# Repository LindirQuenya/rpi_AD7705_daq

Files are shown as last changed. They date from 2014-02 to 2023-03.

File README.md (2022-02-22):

# Data acquisition with the AD7705 on the raspberry PI!

The AD7705 is a two channel sigma delta converter which has
differential inputs, a PGA and programmable data rates. It's
perfect for slowly changing inputs such as pressure, temperature,
heart rate etc.

This repo offers the class `AD7705Comm` which does all the low level
communications with the AD7705. The user just need to register a
callback handler which then returns the samples in realtime.

The class uses the DRDY of the AD7705 connected to Port 22 and
waits for a falling edge on this port to read
the data. This is done via interrupts / poll
so that the ADC process sleeps until new data becomes
available.

## Hardware design

The design files (for EAGLE) are in the subdirectory "pcb".

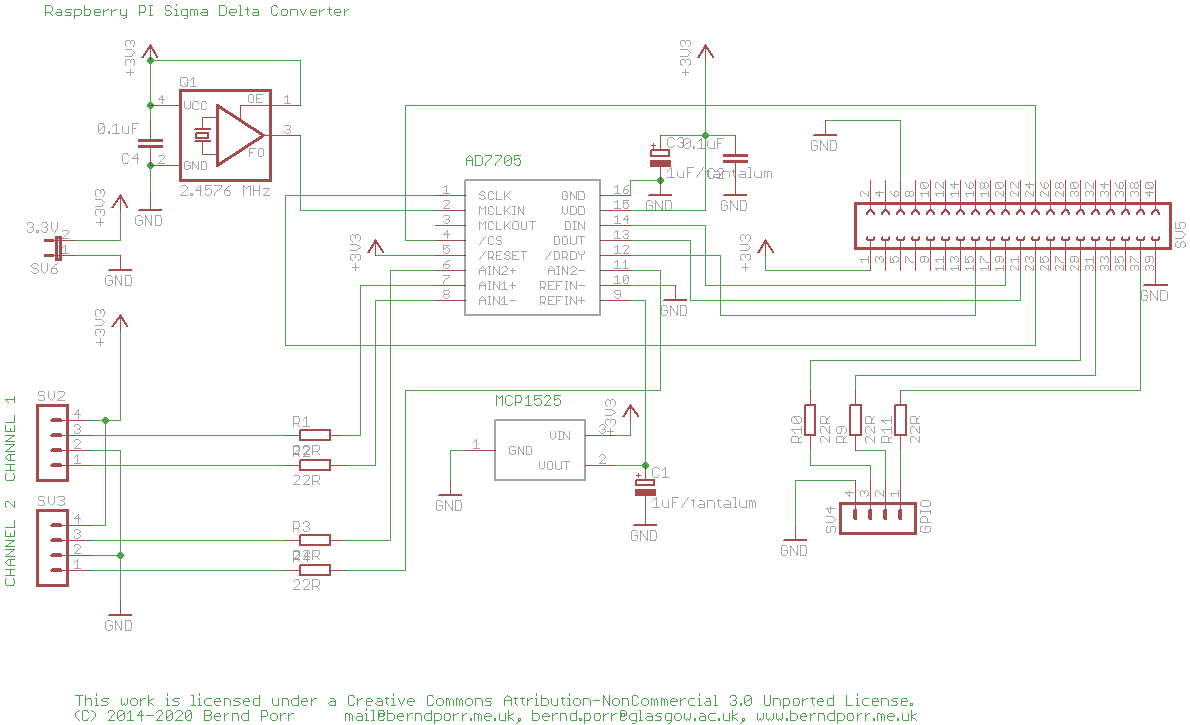
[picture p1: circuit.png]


## Building:

To build:

    cmake .

    make

## Install

    sudo make install

## Usage example

In the subdir example is a simple application which prints the ADC data to the screen.

    cd example
    sudo ./ad7705_printer

## General usage

The online doc is here: http://berndporr.github.io/rpi_AD7705_daq/

### Callback handler

```
class AD7705printSampleCallback : public AD7705callback {
	virtual void hasSample(float v) {
		// process your sample here
	}
};
```

### Main program

Instantiate the AD7705 class and the callback handler:
```
	AD7705Comm ad7705comm;
	AD7705printSampleCallback ad7705printSampleCallback;
	ad7705comm.setCallback(&ad7705printSampleCallback);
```

Start the data acquisition:
```
	ad7705comm.start();
```
once `start` has been called the data will be arriving.

Stop the data acquisition:
```
	ad7705comm.stop();
```

## Author: Bernd Porr

   - bernd.porr@glasgow.ac.uk
   - mail@berndporr.me.uk
   - www.berndporr.me.uk

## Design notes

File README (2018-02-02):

Test / demo program for the AD7705 connected to the raspberry PI!
=================================================================

The AD7705 is a two channel sigma delta converter which has
differential inputs, a PGA and programmable data rates. It's
perfect for slowly changing inputs such as pressure, temperature,
heart rate etc.

The program is interrupt driven and can thus run in a thread
which is woken up by the interrupt. The clock for the ADC is
generated by directly manipulating the registers of the BCM
chip.

This program switches on the clock from the RPI, 
triggers a calibration of the AD, 
reads data from channel 1 and 
prints it on the screen.

This program uses DRDY connected to Port 22 and
waits for a falling edge on this port to read
the data. This is done via interrupts / poll
so that this process sleeps until new data becomes
available.

The design files are in the subdirectory "pcb".



To build:

    make

Run it with the command:

    sudo ./ad7705_test

Associated website:
http://web.eng.gla.ac.uk/rpi/

Bernd Porr
mail@berndporr.me.uk
www.berndporr.me.uk

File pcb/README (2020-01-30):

This work is licensed under a Creative Commons Attribution-NonCommercial 3.0 Unported License.
(C) 2013-2020 BERND PORR, www.berndporr.me.uk

This is an extension board which adds two analogue inputs to the Raspberry PI.
Three GPIO pins are also forwarded to another pin header with additional
input protection.

The AD7705 is a high preceision sigma delta converter with differential
inputs, buffers and a PGA. It's especially designed to measure small voltages,
for example from a pressure gauge or a thermocpuple.

The maximum sampling rate is 500Hz.

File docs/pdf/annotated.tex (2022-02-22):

\doxysection{Class List}
Here are the classes, structs, unions and interfaces with brief descriptions\+:\begin{DoxyCompactList}
\item\contentsline{section}{\mbox{\hyperlink{classAD7705callback}{A\+D7705callback}} \\*Callback for new samples which needs to be implemented by the main program }{\pageref{classAD7705callback}}{}
\item\contentsline{section}{\mbox{\hyperlink{classAD7705Comm}{A\+D7705\+Comm}} \\*This class reads data from the A\+D7705 in the background (separate thread) and calls a callback function whenever data is available }{\pageref{classAD7705Comm}}{}
\item\contentsline{section}{\mbox{\hyperlink{structAD7705settings}{A\+D7705settings}} \\*Contains all settings for the data acquisition }{\pageref{structAD7705settings}}{}
\end{DoxyCompactList}

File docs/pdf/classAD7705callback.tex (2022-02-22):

\hypertarget{classAD7705callback}{}\doxysection{A\+D7705callback Class Reference}
\label{classAD7705callback}\index{AD7705callback@{AD7705callback}}

Callback for new samples which needs to be implemented by the main program.  

{\ttfamily \#include $<$A\+D7705\+Comm.\+h$>$}

\doxysubsection*{Public Member Functions}
\begin{DoxyCompactItemize}
\item 
virtual void \mbox{\hyperlink{classAD7705callback_a0af40415519aef054c0934f6548bab33}{has\+Sample}} (float sample)=0
\begin{DoxyCompactList}\small\item\em Called after a sample has arrived. \end{DoxyCompactList}\end{DoxyCompactItemize}

\doxysubsection{Detailed Description}
Callback for new samples which needs to be implemented by the main program. 

The function has\+Sample needs to be overloaded in the main program. 

\doxysubsection{Member Function Documentation}
\mbox{\Hypertarget{classAD7705callback_a0af40415519aef054c0934f6548bab33}\label{classAD7705callback_a0af40415519aef054c0934f6548bab33}} 
\index{AD7705callback@{AD7705callback}!hasSample@{hasSample}}
\index{hasSample@{hasSample}!AD7705callback@{AD7705callback}}
\doxysubsubsection{\texorpdfstring{hasSample()}{hasSample()}}
{\footnotesize\ttfamily virtual void A\+D7705callback\+::has\+Sample (\begin{DoxyParamCaption}\item[{float}]{sample }\end{DoxyParamCaption})\hspace{0.3cm}{\ttfamily [pure virtual]}}

Called after a sample has arrived. 

\begin{DoxyParams}{Parameters}
{\em sample} & Contains the A\+DC reading in Volt. \\
\hline
\end{DoxyParams}

The documentation for this class was generated from the following file\+:\begin{DoxyCompactItemize}
\item 
A\+D7705\+Comm.\+h\end{DoxyCompactItemize}

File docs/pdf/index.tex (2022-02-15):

The A\+D7705 is a two channel sigma delta converter which has differential inputs, a P\+GA and programmable data rates. It\textquotesingle{}s perfect for slowly changing inputs such as pressure, temperature, heart rate etc.

This repo offers the class {\ttfamily \mbox{\hyperlink{classAD7705Comm}{A\+D7705\+Comm}}} which does all the low level communications with the A\+D7705. The user just need to register a callback handler which then returns the samples in realtime.

The class uses the D\+R\+DY of the A\+D7705 connected to Port 22 and waits for a falling edge on this port to read the data. This is done via interrupts / poll so that the A\+DC process sleeps until new data becomes available.

Github\+: \href{https://github.com/berndporr/rpi_AD7705_daq}{\texttt{ https\+://github.\+com/berndporr/rpi\+\_\+\+A\+D7705\+\_\+daq}}

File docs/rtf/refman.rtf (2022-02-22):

Data acquisition with the AD7705 on the raspberry PI

AUTHOR
Version
Tue Feb 22 2022

Table of Contents

Table of contents

Data acquisition with the AD7705 on the raspberry PI!
The AD7705 is a two channel sigma delta converter which has differential inputs, a PGA and programmable data rates. It's perfect for slowly changing inputs such as pressure, temperature, heart rate etc.
This repo offers the class AD7705Comm which does all the low level communications with the AD7705. The user just need to register a callback handler which then returns the samples in realtime.
The class uses the DRDY of the AD7705 connected to Port 22 and waits for a falling edge on this port to read the data. This is done via interrupts / poll so that the ADC process sleeps until new data becomes available.
Github: https://github.com/berndporr/rpi_AD7705_daq

Class Index
Class List
Here are the classes, structs, unions and interfaces with brief descriptions:
AD7705callback (Callback for new samples which needs to be implemented by the main program ) pagenum
AD7705Comm (This class reads data from the AD7705 in the background (separate thread) and calls a callback function whenever data is available ) pagenum
AD7705settings (Contains all settings for the data acquisition ) pagenum

Class Documentation
AD7705callback Class Reference
AAAAAAAAAAAAAAAAAAAA
Callback for new samples which needs to be implemented by the main program.
#include <AD7705Comm.h>

Public Member Functions
virtual void hasSample (float sample)=0
Called after a sample has arrived.

Detailed Description
Callback for new samples which needs to be implemented by the main program.
The function hasSample needs to be overloaded in the main program.

Member Function Documentation
virtual void AD7705callback::hasSample (float sample)[pure virtual]
AAAAAAAAABAAAAAAAAAB
Called after a sample has arrived.

Parameters
sample | Contains the ADC reading in Volt.

The documentation for this class was generated from the following file:
AD7705Comm.h

AD7705Comm Class Reference
AAAAAAAAACAAAAAAAAAC
This class reads data from the AD7705 in the background (separate thread) and calls a callback function whenever data is available.
#include <AD7705Comm.h>

Public Member Functions
AD7705Comm (AD7705settings settings)
Constructor.

~AD7705Comm ()AAAAAAAAADAAAAAAAAAD
Destructor which makes sure the data acquisition has stopped.

void registerCallback (AD7705callback *cb)
Registers the callback which is called whenever there is a sample.

void unRegisterCallback ()AAAAAAAAAEAAAAAAAAAE
Unregisters the callback to the callback interface.

void start ()AAAAAAAAAFAAAAAAAAAF
Starts the data acquisition.

void stop ()AAAAAAAAAGAAAAAAAAAG
Stops the data acquistion.

Detailed Description
This class reads data from the AD7705 in the background (separate thread) and calls a callback function whenever data is available.

Constructor & Destructor Documentation
AD7705Comm::AD7705Comm (AD7705settings settings)
AAAAAAAAAHAAAAAAAAAH
Constructor.
Opens the SPI device and waits for to start the acquisition.
Parameters
settings | All AD7705 settings.

Member Function Documentation
void AD7705Comm::registerCallback (AD7705callback * cb)
AAAAAAAAAIAAAAAAAAAI
Registers the callback which is called whenever there is a sample.

Parameters
cb | Pointer to the callback interface.

The documentation for this class was generated from the following file:
AD7705Comm.h

AD7705settings Struct Reference
AAAAAAAAAJAAAAAAAAAJ
Contains all settings for the data acquisition.
#include <AD7705Comm.h>

Public Types
enum SamplingRates { FS50HZ = 0, FS60HZ = 1, FS250HZ = 2, FS500HZ = 3 }AAAAAAAAAKAAAAAAAAAK
Sampling rates.
enum PGAGains { G1 = 0, G2 = 1, G4 = 2, G8 = 3, G16 = 4, G32 = 5, G64 = 6, G128 = 7 }AAAAAAAAALAAAAAAAAAL
Gains of the PGA.
enum AIN { AIN1 = 0, AIN2 = 1 }AAAAAAAAAMAAAAAAAAAM
Channel indices.
enum Modes { Bipolar = 0, Unipolar = 1 }AAAAAAAAANAAAAAAAAAN
Unipolar or bipolar mode.
Public Attributes
std::string spiDevice = "/dev/spidev0.0"AAAAAAAAAOAAAAAAAAAO
The SPI device in /dev used.

SamplingRates samplingRate = FS50HZAAAAAAAAAPAAAAAAAAAP
Sampling rate requested.

PGAGains pgaGain = G1AAAAAAAAAQAAAAAAAAAQ
Requested gain.

AIN channel = AIN1AAAAAAAAARAAAAAAAAAR
Requested input channel (0 or 1)

Modes mode = UnipolarAAAAAAAAASAAAAAAAAAS
Unipolar or biploar.

Detailed Description
Contains all settings for the data acquisition.

The documentation for this struct was generated from the following file:
AD7705Comm.h

Index
INDEX

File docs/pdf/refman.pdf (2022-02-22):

## Data acquisition with the AD7705 on the raspberry PI

Generated by Doxygen 1.8.17

i

1 Data acquisition with the AD7705 on the raspberry PI! | 1
2 Class Index | 3
3 Class Documentation | 5
Index | 9

Generated by Doxygen

# Chapter 1

# Data acquisition with the AD7705 on the raspberry

PI!

The AD7705 is a two channel sigma delta converter which has differential inputs, a PGA and programmable data rates. It's perfect for slowly changing inputs such as pressure, temperature, heart rate etc.

This repo offers the class AD7705Comm which does all the low level communications with the AD7705. The user just need to register a callback handler which then returns the samples in realtime.

The class uses the DRDY of the AD7705 connected to Port 22 and waits for a falling edge on this port to read the data. This is done via interrupts / poll so that the ADC process sleeps until new data becomes available.

Github: https://github.com/berndporr/rpi_AD7705_daq

### 2 Data acquisition with the AD7705 on the raspberry PI!

# Chapter 2

# Class Index

## 2.1 Class List

Here are the classes, structs, unions and interfaces with brief descriptions:

AD7705callback

AD7705Comm
This class reads data from the AD7705 in the background (separate thread) and calls a callback

AD7705settings

### 4 Class Index

# Chapter 3

# Class Documentation

## 3.1 AD7705callback Class Reference

Callback for new samples which needs to be implemented by the main program.

#include <AD7705Comm.h>

Public Member Functions

- virtual void hasSample (float sample)=0

Called after a sample has arrived.

### 3.1.1 Detailed Description

Callback for new samples which needs to be implemented by the main program.

The function hasSample needs to be overloaded in the main program.

### 3.1.2 Member Function Documentation

### 3.1.2.1 hasSample()

virtual void AD7705callback::hasSample (

float sample ) [pure virtual]

Called after a sample has arrived.

Parameters

sample Contains the ADC reading in Volt.

### 6 Class Documentation

The documentation for this class was generated from the following file:

- AD7705Comm.h

## 3.2 AD7705Comm Class Reference

This class reads data from the AD7705 in the background (separate thread) and calls a callback function whenever data is available.

#include <AD7705Comm.h>

Public Member Functions

- AD7705Comm (AD7705settings settings)

Constructor.
- ∼AD7705Comm ()

Destructor which makes sure the data acquisition has stopped.
- void registerCallback (AD7705callback ∗cb)

Registers the callback which is called whenever there is a sample.
- void unRegisterCallback ()

Unregisters the callback to the callback interface.
- void start ()

Starts the data acquisition.
- void stop ()

Stops the data acquistion.

### 3.2.1 Detailed Description

This class reads data from the AD7705 in the background (separate thread) and calls a callback function whenever data is available.

### 3.2.2 Constructor & Destructor Documentation

### 3.2.2.1 AD7705Comm()

AD7705Comm::AD7705Comm (

AD7705settings settings )

Constructor.

Opens the SPI device and waits for to start the acquisition.

3.3 AD7705settings Struct Reference | 7

Parameters

settings All AD7705 settings.

### 3.2.3 Member Function Documentation

### 3.2.3.1 registerCallback()

void AD7705Comm::registerCallback (

AD7705callback ∗ cb )

Registers the callback which is called whenever there is a sample.

Parameters

cb Pointer to the callback interface.

The documentation for this class was generated from the following file:

- AD7705Comm.h

## 3.3 AD7705settings Struct Reference

Contains all settings for the data acquisition.

#include <AD7705Comm.h>

Public Types

- enum SamplingRates { FS50HZ = 0, FS60HZ = 1, FS250HZ = 2, FS500HZ = 3 }

Sampling rates.
- enum PGAGains {
G1 = 0, G2 = 1, G4 = 2, G8 = 3,
G16 = 4, G32 = 5, G64 = 6, G128 = 7 }

Gains of the PGA.
- enum AIN { AIN1 = 0, AIN2 = 1 }

Channel indices.
- enum Modes { Bipolar = 0, Unipolar = 1 }

Unipolar or bipolar mode.

### 8 Class Documentation

Public Attributes

- std::string spiDevice = "/dev/spidev0.0"

The SPI device in /dev used.
- SamplingRates samplingRate = FS50HZ

Sampling rate requested.
- PGAGains pgaGain = G1

Requested gain.
- AIN channel = AIN1

Requested input channel (0 or 1)
- Modes mode = Unipolar

Unipolar or biploar.

### 3.3.1 Detailed Description

Contains all settings for the data acquisition.

The documentation for this struct was generated from the following file:

- AD7705Comm.h

# Index

AD7705callback, 5
hasSample, 5
AD7705Comm, 6
AD7705Comm, 6
registerCallback, 7
AD7705settings, 7

hasSample
AD7705callback, 5

registerCallback
AD7705Comm, 7

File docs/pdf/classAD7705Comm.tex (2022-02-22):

\hypertarget{classAD7705Comm}{}\doxysection{A\+D7705\+Comm Class Reference}
\label{classAD7705Comm}\index{AD7705Comm@{AD7705Comm}}

This class reads data from the A\+D7705 in the background (separate thread) and calls a callback function whenever data is available.  

{\ttfamily \#include $<$A\+D7705\+Comm.\+h$>$}

\doxysubsection*{Public Member Functions}
\begin{DoxyCompactItemize}
\item 
\mbox{\hyperlink{classAD7705Comm_a1d06fa3bdea3ee1616dcab0f406aca8a}{A\+D7705\+Comm}} (\mbox{\hyperlink{structAD7705settings}{A\+D7705settings}} settings)
\begin{DoxyCompactList}\small\item\em Constructor. \end{DoxyCompactList}\item 
\mbox{\Hypertarget{classAD7705Comm_a6f101db8298da94c1bb82c2735015eb1}\label{classAD7705Comm_a6f101db8298da94c1bb82c2735015eb1}} 
\mbox{\hyperlink{classAD7705Comm_a6f101db8298da94c1bb82c2735015eb1}{$\sim$\+A\+D7705\+Comm}} ()
\begin{DoxyCompactList}\small\item\em Destructor which makes sure the data acquisition has stopped. \end{DoxyCompactList}\item 
void \mbox{\hyperlink{classAD7705Comm_a3bf730b355147bde014465c37b17623a}{register\+Callback}} (\mbox{\hyperlink{classAD7705callback}{A\+D7705callback}} $\ast$cb)
\begin{DoxyCompactList}\small\item\em Registers the callback which is called whenever there is a sample. \end{DoxyCompactList}\item 
\mbox{\Hypertarget{classAD7705Comm_a302b3a43102d7675a4f27382f388d1b4}\label{classAD7705Comm_a302b3a43102d7675a4f27382f388d1b4}} 
void \mbox{\hyperlink{classAD7705Comm_a302b3a43102d7675a4f27382f388d1b4}{un\+Register\+Callback}} ()
\begin{DoxyCompactList}\small\item\em Unregisters the callback to the callback interface. \end{DoxyCompactList}\item 
\mbox{\Hypertarget{classAD7705Comm_affc6ded162b91b5e55ed791451ef2373}\label{classAD7705Comm_affc6ded162b91b5e55ed791451ef2373}} 
void \mbox{\hyperlink{classAD7705Comm_affc6ded162b91b5e55ed791451ef2373}{start}} ()
\begin{DoxyCompactList}\small\item\em Starts the data acquisition. \end{DoxyCompactList}\item 
\mbox{\Hypertarget{classAD7705Comm_a6817c77451e4a0f7a85a79c1c39d158e}\label{classAD7705Comm_a6817c77451e4a0f7a85a79c1c39d158e}} 
void \mbox{\hyperlink{classAD7705Comm_a6817c77451e4a0f7a85a79c1c39d158e}{stop}} ()
\begin{DoxyCompactList}\small\item\em Stops the data acquistion. \end{DoxyCompactList}\end{DoxyCompactItemize}

\doxysubsection{Detailed Description}
This class reads data from the A\+D7705 in the background (separate thread) and calls a callback function whenever data is available. 

\doxysubsection{Constructor \& Destructor Documentation}
\mbox{\Hypertarget{classAD7705Comm_a1d06fa3bdea3ee1616dcab0f406aca8a}\label{classAD7705Comm_a1d06fa3bdea3ee1616dcab0f406aca8a}} 
\index{AD7705Comm@{AD7705Comm}!AD7705Comm@{AD7705Comm}}
\index{AD7705Comm@{AD7705Comm}!AD7705Comm@{AD7705Comm}}
\doxysubsubsection{\texorpdfstring{AD7705Comm()}{AD7705Comm()}}
{\footnotesize\ttfamily A\+D7705\+Comm\+::\+A\+D7705\+Comm (\begin{DoxyParamCaption}\item[{\mbox{\hyperlink{structAD7705settings}{A\+D7705settings}}}]{settings }\end{DoxyParamCaption})}

Constructor. 

Opens the S\+PI device and waits for to start the acquisition. 
\begin{DoxyParams}{Parameters}
{\em settings} & All A\+D7705 settings. \\
\hline
\end{DoxyParams}

\doxysubsection{Member Function Documentation}
\mbox{\Hypertarget{classAD7705Comm_a3bf730b355147bde014465c37b17623a}\label{classAD7705Comm_a3bf730b355147bde014465c37b17623a}} 
\index{AD7705Comm@{AD7705Comm}!registerCallback@{registerCallback}}
\index{registerCallback@{registerCallback}!AD7705Comm@{AD7705Comm}}
\doxysubsubsection{\texorpdfstring{registerCallback()}{registerCallback()}}
{\footnotesize\ttfamily void A\+D7705\+Comm\+::register\+Callback (\begin{DoxyParamCaption}\item[{\mbox{\hyperlink{classAD7705callback}{A\+D7705callback}} $\ast$}]{cb }\end{DoxyParamCaption})}

Registers the callback which is called whenever there is a sample. 

\begin{DoxyParams}{Parameters}
{\em cb} & Pointer to the callback interface. \\
\hline
\end{DoxyParams}

The documentation for this class was generated from the following file\+:\begin{DoxyCompactItemize}
\item 
A\+D7705\+Comm.\+h\end{DoxyCompactItemize}

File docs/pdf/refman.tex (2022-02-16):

\let\mypdfximage\pdfximage\def\pdfximage{\immediate\mypdfximage}\documentclass[twoside]{book}

%% moved from doxygen.sty due to workaround for LaTex 2019 version and unmaintained tabu package
\usepackage{ifthen}
\ifx\requestedLaTeXdate\undefined
\usepackage{array}
\else
\usepackage{array}[=2016-10-06]
\fi
%%
% Packages required by doxygen
\usepackage{fixltx2e}
\usepackage{calc}
\usepackage{doxygen}
\usepackage{graphicx}
\usepackage[utf8]{inputenc}
\usepackage{makeidx}
\usepackage{multicol}
\usepackage{multirow}
\PassOptionsToPackage{warn}{textcomp}
\usepackage{textcomp}
\usepackage[nointegrals]{wasysym}
\usepackage[table]{xcolor}
\usepackage{ifpdf,ifxetex}

% Font selection
\usepackage[T1]{fontenc}
\usepackage[scaled=.90]{helvet}
\usepackage{courier}
\usepackage{amssymb}
\usepackage{sectsty}
\renewcommand{\familydefault}{\sfdefault}
\allsectionsfont{%
  \fontseries{bc}\selectfont%
  \color{darkgray}%
}
\renewcommand{\DoxyLabelFont}{%
  \fontseries{bc}\selectfont%
  \color{darkgray}%
}
\newcommand{\+}{\discretionary{\mbox{\scriptsize$\hookleftarrow$}}{}{}}

% Arguments of doxygenemoji:
% 1) ':<text>:' form of the emoji, already "LaTeX"-escaped
% 2) file with the name of the emoji without the .png extension
% in case image exist use this otherwise use the ':<text>:' form
\newcommand{\doxygenemoji}[2]{%
  \IfFileExists{./#2.png}{\raisebox{-0.1em}{}}{#1}%
}
% Page & text layout
\usepackage{geometry}
\geometry{%
  a4paper,%
  top=2.5cm,%
  bottom=2.5cm,%
  left=2.5cm,%
  right=2.5cm%
}
\tolerance=750
\hfuzz=15pt
\hbadness=750
\setlength{\emergencystretch}{15pt}
\setlength{\parindent}{0cm}
\newcommand{\doxynormalparskip}{\setlength{\parskip}{3ex plus 2ex minus 2ex}}
\newcommand{\doxytocparskip}{\setlength{\parskip}{1ex plus 0ex minus 0ex}}
\doxynormalparskip
\makeatletter
\renewcommand{\paragraph}{%
  \@startsection{paragraph}{4}{0ex}{-1.0ex}{1.0ex}{%
    \normalfont\normalsize\bfseries\SS@parafont%
  }%
}
\renewcommand{\subparagraph}{%
  \@startsection{subparagraph}{5}{0ex}{-1.0ex}{1.0ex}{%
    \normalfont\normalsize\bfseries\SS@subparafont%
  }%
}
\makeatother

\makeatletter
\newcommand\hrulefilll{\leavevmode\leaders\hrule\hskip 0pt plus 1filll\kern\z@}
\makeatother

% Headers & footers
\usepackage{fancyhdr}
\pagestyle{fancyplain}
\fancyhead[LE]{\fancyplain{}{\bfseries\thepage}}
\fancyhead[CE]{\fancyplain{}{}}
\fancyhead[RE]{\fancyplain{}{\bfseries\leftmark}}
\fancyhead[LO]{\fancyplain{}{\bfseries\rightmark}}
\fancyhead[CO]{\fancyplain{}{}}
\fancyhead[RO]{\fancyplain{}{\bfseries\thepage}}
\fancyfoot[LE]{\fancyplain{}{}}
\fancyfoot[CE]{\fancyplain{}{}}
\fancyfoot[RE]{\fancyplain{}{\bfseries\scriptsize Generated by Doxygen }}
\fancyfoot[LO]{\fancyplain{}{\bfseries\scriptsize Generated by Doxygen }}
\fancyfoot[CO]{\fancyplain{}{}}
\fancyfoot[RO]{\fancyplain{}{}}
\renewcommand{\footrulewidth}{0.4pt}
\renewcommand{\chaptermark}[1]{%
  \markboth{#1}{}%
}
\renewcommand{\sectionmark}[1]{%
  \markright{\thesection\ #1}%
}

% Indices & bibliography
\usepackage{natbib}
\usepackage[titles]{tocloft}
\setcounter{tocdepth}{3}
\setcounter{secnumdepth}{5}
\makeindex

\usepackage{newunicodechar}
  \newunicodechar{⁻}{${}^{-}$}% Superscript minus
  \newunicodechar{²}{${}^{2}$}% Superscript two
  \newunicodechar{³}{${}^{3}$}% Superscript three

% Hyperlinks (required, but should be loaded last)
\ifpdf
  \usepackage[pdftex,pagebackref=true]{hyperref}
\else
  \ifxetex
    \usepackage[pagebackref=true]{hyperref}
  \else
    \usepackage[ps2pdf,pagebackref=true]{hyperref}
  \fi
\fi

\hypersetup{%
  colorlinks=true,%
  linkcolor=blue,%
  citecolor=blue,%
  unicode%
}

% Custom commands
\newcommand{\clearemptydoublepage}{%
  \newpage{\pagestyle{empty}\cleardoublepage}%
}

\usepackage{caption}
\captionsetup{labelsep=space,justification=centering,font={bf},singlelinecheck=off,skip=4pt,position=top}

\usepackage{etoc}
\etocsettocstyle{\doxytocparskip}{\doxynormalparskip}
\renewcommand{\numberline}[1]{#1~}
%===== C O N T E N T S =====

\begin{document}

% Titlepage & ToC
\hypersetup{pageanchor=false,
             bookmarksnumbered=true,
             pdfencoding=unicode
            }
\pagenumbering{alph}
\begin{titlepage}
\vspace*{7cm}
\begin{center}%
{\Large Data acquisition with the A\+D7705 on the raspberry PI }\\
\vspace*{1cm}
{\large Generated by Doxygen 1.8.17}\\
\end{center}
\end{titlepage}
\clearemptydoublepage
\pagenumbering{roman}
\tableofcontents
\clearemptydoublepage
\pagenumbering{arabic}
\hypersetup{pageanchor=true}

%--- Begin generated contents ---
\chapter{Data acquisition with the A\+D7705 on the raspberry P\+I!}
\label{index}\hypertarget{index}{}\input{index}
\chapter{Class Index}
\input{annotated}
\chapter{Class Documentation}
\input{classAD7705callback}
\input{classAD7705Comm}
\input{structAD7705settings}
%--- End generated contents ---

% Index
\backmatter
\newpage
\phantomsection
\clearemptydoublepage
\addcontentsline{toc}{chapter}{\indexname}
\printindex

\end{document}

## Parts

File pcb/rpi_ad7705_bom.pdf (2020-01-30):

Sheet1

Page 1

rpi_ad7705

Qty | Value | Device | Parts | Farnell | RS
3 | MA04-1 | SV2, SV3
| 2 0.1uF | C5/2.5 | C2,C4
| 2 1uF/tantalum | CPOL-EUTT2D7 | C1, C3
| 1 3.3V | JP1E | SV6
| 7 22R | R-EU_0207/10 | R1, R2, R3, R4, R9, R10, R11
| 1 AD7705 | AD7705 | U$1 | SC03234 | 523-8446
| 1 MCP1525 | MCP1525 | U$2 | 1292235 | 738-6358
| 1 RASPBERRY PI | FE13-2 | SV1 | 9138676
| 12.4576 MHz | X1G004451004512 | Q1 | 2506984

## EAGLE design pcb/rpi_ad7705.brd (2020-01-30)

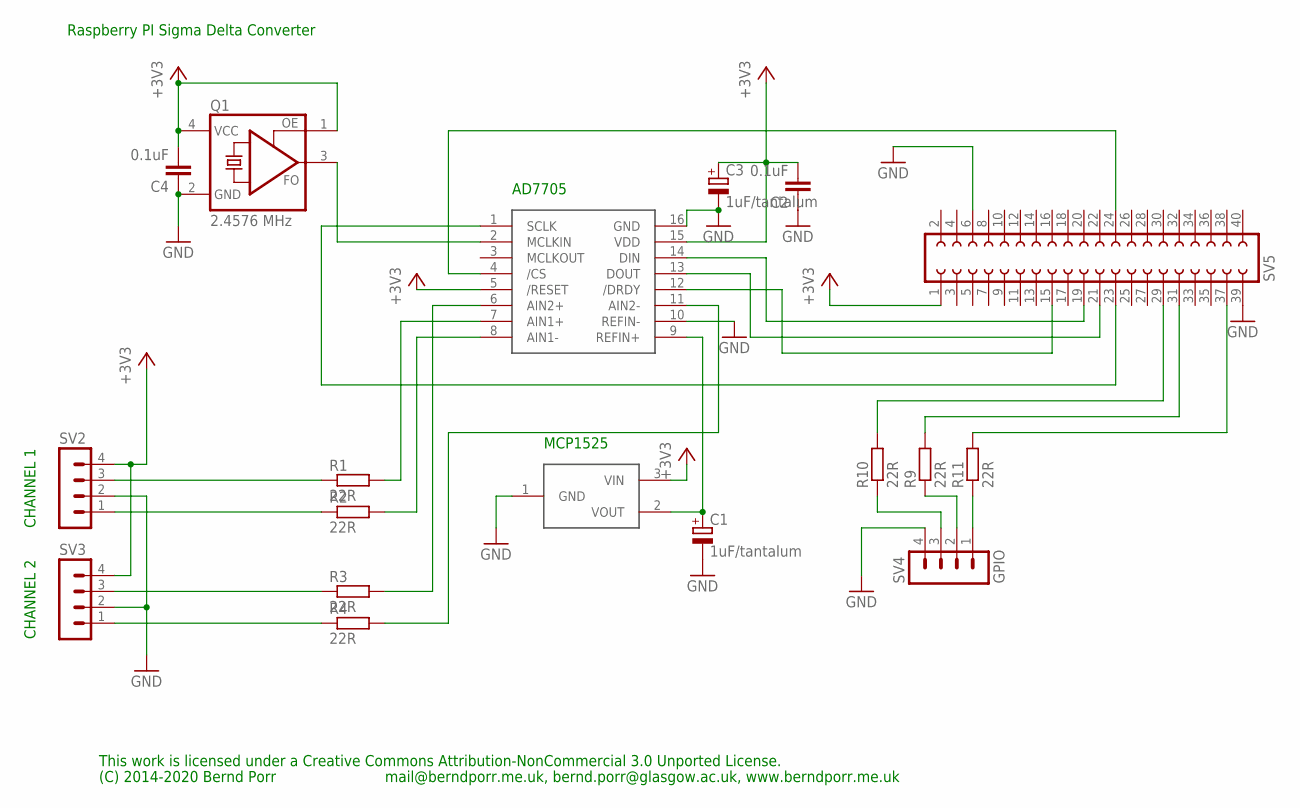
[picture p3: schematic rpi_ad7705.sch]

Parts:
C1, C3: 1uF/tantalum; TT2D7
C2, C4: 0.1uF; C5B2.5
Q1: 2.4576 MHz; ASF
R1, R2, R3, R4, R9, R10, R11: 22R; 0207/10
SV2, SV3: MA04-1
SV4: GPIO; MA04-1
SV5: FE20-2
U$1: AD7705; DIP16
U$2: MCP1525; TO92

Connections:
+3V3: C2.2, C3.+, C4.2, Q1.1 (OE), Q1.4 (VCC), SV2.4, SV3.4, SV5.1, U$1.5 (/RESET), U$1.15 (VDD), U$2.3 (VIN)
GND: C1.-, C2.1, C3.-, C4.1, Q1.2 (GND), SV2.2, SV3.2, SV4.4, SV5.6, SV5.39, U$1.10 (REFIN-), U$1.16 (GND), U$2.1 (GND)
unnamed: SV5.19, U$1.14 (DIN)
unnamed: SV5.23, U$1.1 (SCLK)
unnamed: Q1.3 (FO), U$1.2 (MCLKIN)
unnamed: SV5.24, U$1.4 (/CS)
unnamed: R11.2, SV5.37
unnamed: SV5.21, U$1.13 (DOUT)
unnamed: R2.2, U$1.8 (AIN1-)
unnamed: R1.2, U$1.7 (AIN1+)
unnamed: R3.2, U$1.6 (AIN2+)
unnamed: R4.2, U$1.11 (AIN2-)
unnamed: R1.1, SV2.3
unnamed: R2.1, SV2.1
unnamed: R3.1, SV3.3
unnamed: R4.1, SV3.1
unnamed: R10.1, SV4.3
unnamed: R9.2, SV5.31
unnamed: R10.2, SV5.29
unnamed: R11.1, SV4.1
unnamed: R9.1, SV4.2
unnamed: SV5.15, U$1.12 (/DRDY)
unnamed: C1.+, U$1.9 (REFIN+), U$2.2 (VOUT)

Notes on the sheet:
This work is licensed under a Creative Commons Attribution-NonCommercial 3.0 Unported License.
(C) 2014-2020 Bernd Porr
mail@berndporr.me.uk, bernd.porr@glasgow.ac.uk, www.berndporr.me.uk
AD7705
MCP1525
CHANNEL 1
CHANNEL 2
Raspberry PI Sigma Delta Converter

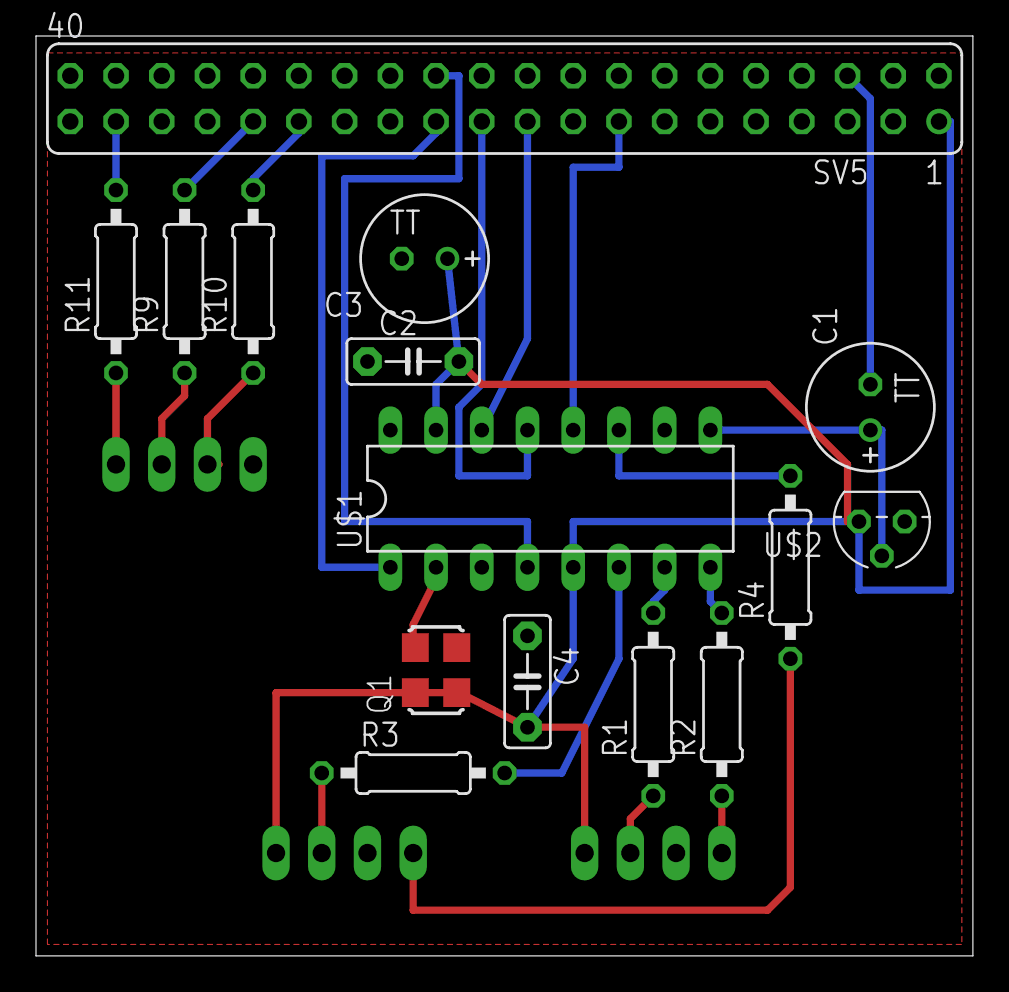
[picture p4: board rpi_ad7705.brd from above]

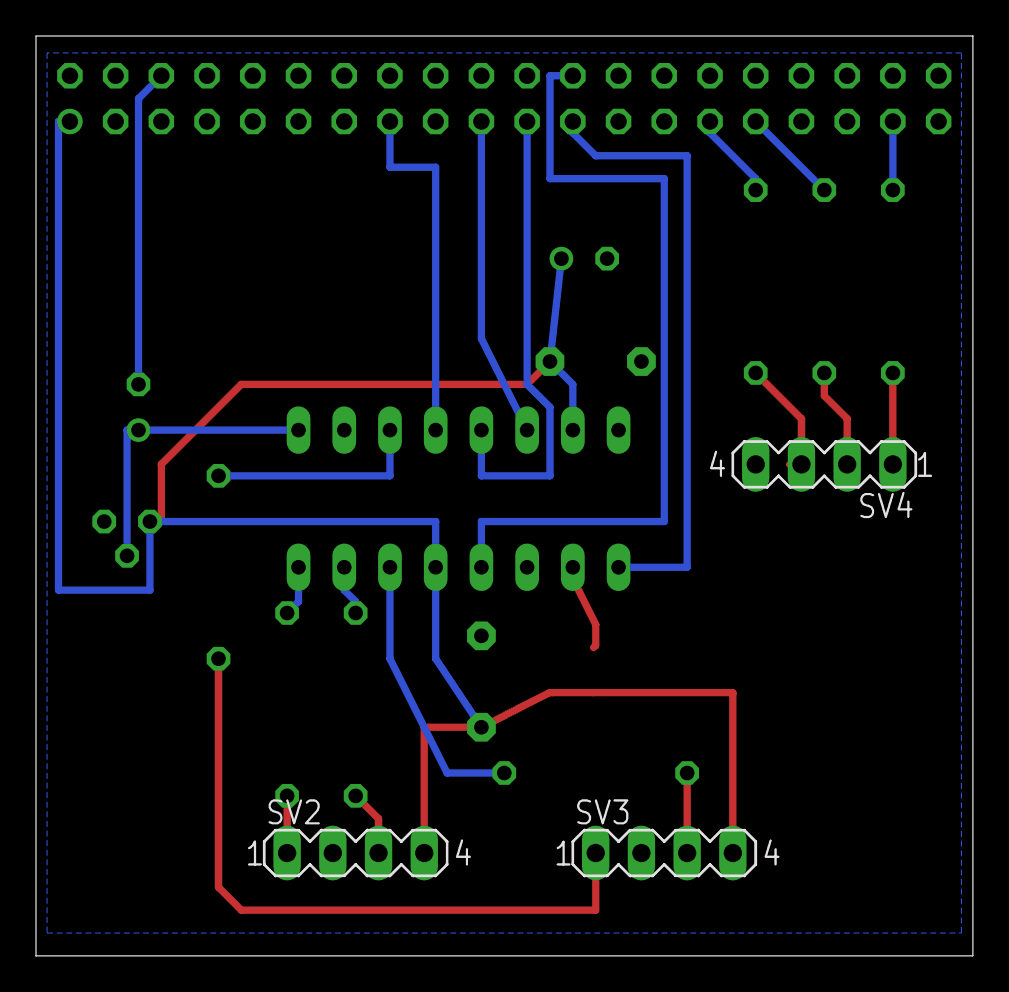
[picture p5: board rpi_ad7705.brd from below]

Board: 2 copper layers, 52.0 x 51.1 mm, 18 parts (3 on the bottom side), 23 nets.

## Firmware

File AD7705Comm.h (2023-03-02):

#ifndef __AD7705COMM_H
#define __AD7705COMM_H

/*
 * AD7705 class to read data at a given sampling rate
 *
 * Copyright (c) 2007  MontaVista Software, Inc.
 * Copyright (c) 2007  Anton Vorontsov <avorontsov@ru.mvista.com>
 * Copyright (c) 2013-2022  Bernd Porr <mail@berndporr.me.uk>
 *
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
 */
#include <stdint.h>
#include <unistd.h>
#include <stdio.h>
#include <stdlib.h>
#include <fcntl.h>
#include <sys/ioctl.h>
#include <linux/types.h>
#include <linux/spi/spidev.h>
#include <thread>  
#include <string>

#ifndef NDEBUG
#define DEBUG
#endif


/**
 * Callback for new samples which needs to be implemented by the main program.
 * The function hasSample needs to be overloaded in the main program.
 **/
class AD7705callback {
public:
	/**
	 * Called after a sample has arrived.
	 * \param sample Contains the ADC reading in Volt.
	 **/
	virtual void hasSample(float sample) = 0;
};


/**
 * Contains all settings for the data acquisition.
 **/
struct AD7705settings {
	/**
	 * The SPI device in /dev used.
	 **/
	std::string spiDevice = "/dev/spidev0.0";
	
	/**
	 * Sampling rates
	 **/
	enum SamplingRates {
		FS50HZ  = 0,
		FS60HZ  = 1,
		FS250HZ = 2,
		FS500HZ = 3
	};

	/**
	 * Sampling rate requested
	 **/
	SamplingRates samplingRate = FS50HZ;

	/**
	 * Gains of the PGA
	 **/
	enum PGAGains {
		G1   = 0,
		G2   = 1,
		G4   = 2,
		G8   = 3,
		G16  = 4,
		G32  = 5,
		G64  = 6,
		G128 = 7
	};

	/**
	 * Requested gain
	 **/
	PGAGains pgaGain = G1;

	/**
	 * Channel indices
	 **/
	enum AIN {
		AIN1 = 0,
		AIN2 = 1
	};

	/**
	 * Requested input channel (0 or 1)
	 **/
	AIN channel = AIN1;

	/**
	 * Unipolar or bipolar mode
	 **/
	enum Modes {
		Bipolar  = 0,
		Unipolar = 1
	};

	/**
	 * Unipolar or biploar
	 **/
	Modes mode = Unipolar;
};


/**
 * This class reads data from the AD7705 in the background (separate
 * thread) and calls a callback function whenever data is available.
 **/
class AD7705Comm {

public:
	/**
	 * Constructor. Opens the SPI device and waits for to start
	 * the acquisition.
	 * \param settings All AD7705 settings.
	 **/
	AD7705Comm(AD7705settings settings);

	/**
	 * Destructor which makes sure the data acquisition
	 * has stopped.
	 **/
	~AD7705Comm();
       
	/**
	 * Registers the callback which is called whenever there is a sample.
	 * \param cb Pointer to the callback interface.
	 **/
	void registerCallback(AD7705callback* cb);

	/**
	 * Unregisters the callback to the callback interface.
	 **/
	void unRegisterCallback();

	/**
	 * Starts the data acquisition
	 **/
	void start();

	/**
	 * Stops the data acquistion
	 **/
	void stop();

private:
	const uint8_t mode = SPI_CPHA | SPI_CPOL;
	const int drdy_GPIO = 22;
	const uint32_t speed = 500000;
	const uint16_t delay = 0;
	const uint8_t bpw   = 8;
	static constexpr float ADC_REF = 2.5;
	int fd = 0;
	std::thread daqThread;
	int running = 0;
	AD7705callback* ad7705callback = nullptr;
	AD7705settings ad7705settings;

	int spi_transfer(int fd, uint8_t* tx, uint8_t* rx, int n);
	void writeReset(int fd);
	void writeReg(int fd, uint8_t v);
	uint8_t readReg(int fd);
	int16_t readData(int fd);
	void run();

        inline float pgaGain() {
		return (float)(1 << ad7705settings.pgaGain);
	}

	inline uint8_t commReg() {
		return ((uint8_t)(ad7705settings.channel));
	}

	static int getSysfsIRQfd(int gpio);
	static int fdPoll(int gpio_fd, int timeoutus);
	static void gpio_unexport(int gpio);
};


#endif

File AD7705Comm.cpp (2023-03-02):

#include "AD7705Comm.h"

#include <fcntl.h>
#include <poll.h>
#include <string.h>

#define SYSFS_GPIO_DIR "/sys/class/gpio"
#define MAX_BUF 256

AD7705Comm::AD7705Comm(AD7705settings settings) {
	fd = open(settings.spiDevice.c_str(), O_RDWR);
	if (fd < 0)
		throw "Can't open device";
	
	// set SPI mode
	int ret = ioctl(fd, SPI_IOC_WR_MODE, &mode);
	if (ret == -1) {
		throw "can't set spi mode";
	} else {
#ifdef DEBUG
		fprintf(stderr,"SPI mode %d set (ret=%d).\n",mode,ret);
#endif
	}
}

AD7705Comm::~AD7705Comm() {
	stop();
	close(fd);
}


void AD7705Comm::registerCallback(AD7705callback* cb) {
	ad7705callback = cb;
}

void AD7705Comm::unRegisterCallback() {
	ad7705callback = nullptr;
}

int AD7705Comm::spi_transfer(int fd, uint8_t* tx, uint8_t* rx, int n) {
	struct spi_ioc_transfer tr;
	memset(&tr,0,sizeof(struct spi_ioc_transfer));
	tr.tx_buf = (unsigned long)tx;
	tr.rx_buf = (unsigned long)rx;
	tr.len = n;
	tr.delay_usecs = delay;
	tr.speed_hz = speed;
	tr.bits_per_word = bpw;	
	int ret = ioctl(fd, SPI_IOC_MESSAGE(1), &tr);
	return ret;
}

void AD7705Comm::writeReset(int fd) {
	uint8_t tx[5] = {0xff,0xff,0xff,0xff,0xff};
	uint8_t rx[5] = {0};
	
	int ret = spi_transfer(fd, tx, rx, 5);
	
	if (ret < 1) {
#ifdef DEBUG
		printf("\nerr=%d when trying to reset. \n",ret);
#endif
		throw "Can't send spi message";
	}
}

void AD7705Comm::writeReg(int fd, uint8_t v) {
	uint8_t tx = v;
	uint8_t rx = 0;
	
	int ret = spi_transfer(fd, &tx, &rx, 1);
	if (ret < 1)
		throw "can't send spi message";
}

uint8_t AD7705Comm::readReg(int fd) {
	uint8_t tx = 0;
	uint8_t rx = 0;
	
	int ret = spi_transfer(fd, &tx, &rx, 1);
		if (ret < 1)
			throw "can't send spi message";
		
		return rx;
}

int16_t AD7705Comm::readData(int fd) {
	uint8_t tx[2] = {0,0};
		uint8_t rx[2] = {0,0};
		
		int ret = spi_transfer(fd, tx, rx, 2);
		if (ret < 1) {
			printf("\n can't send spi message, ret = %d\n",ret);
			throw "Can't send spi message";
		}
		
		return (rx[0]<<8)|(rx[1]);
}


void AD7705Comm::run() {
	// get a file descriptor for the IRQ GPIO pin
	int sysfs_fd = getSysfsIRQfd(drdy_GPIO);
	running = 1;
	while (running) {
		// let's wait for data for max one second
		// goes to sleep until an interrupt happens
		int ret = fdPoll(sysfs_fd,1000);
		if (ret<1) {
#ifdef DEBUG
			fprintf(stderr,"Poll error %d\n",ret);
#endif
			throw "Interrupt timeout";
		}
		
		// tell the AD7705 to read the data register (16 bits)
		writeReg(fd, commReg() | 0x38);
		// read the data register by performing two 8 bit reads
		const float norm = 0x8000;
		const float value =(readData(fd))/norm *
			ADC_REF / pgaGain();
		if (nullptr != ad7705callback) {
			ad7705callback->hasSample(value);
		}
	}
	close(sysfs_fd);
	gpio_unexport(drdy_GPIO);
}


void AD7705Comm::start() {
  if (running) return;

#ifdef DEBUG
	fprintf(stderr,"Sending reset.\n");
#endif
	writeReset(fd);

	// tell the AD7705 that the next write will be to the clock register
	writeReg(fd,commReg() | 0x20);
	// write 00000100 : CLOCKDIV=0,CLK=1,expects 4.9152MHz input clock, sampling rate
	writeReg(fd,0x04 | ad7705settings.samplingRate);
	
	// tell the AD7705 that the next write will be the setup register
	writeReg(fd,commReg() | 0x10);
	// intiates a self calibration and then converting starts
	writeReg(fd,0x40 | (ad7705settings.mode << 2) | ( ad7705settings.pgaGain << 3) );

#ifdef DEBUG
	fprintf(stderr,"Starting DAQ thread.\n");
#endif
	
	daqThread = std::thread(&AD7705Comm::run,this);
}


void AD7705Comm::stop() {
	if (!running) return;
	running = 0;
	daqThread.join();
#ifdef DEBUG
	fprintf(stderr,"DAQ thread stopped.\n");
#endif	
}

int AD7705Comm::getSysfsIRQfd(int gpio) {
	  int fd, len;
	  char buf[MAX_BUF];
 
	  fd = open(SYSFS_GPIO_DIR "/export", O_WRONLY);
	  if (fd < 0) {
#ifdef DEBUG
		  perror("gpio/export");
#endif
		  return fd;
	  }
	  
	  len = snprintf(buf, sizeof(buf), "%d", gpio);
	  int r = write(fd, buf, len);
	  close(fd);
	  if (r < 0) {
#ifdef DEBUG
		  perror("gpio/export");
#endif
		  return fd;
	  }
 
	  snprintf(buf, sizeof(buf), SYSFS_GPIO_DIR  "/gpio%d/direction", gpio);
	  
	  fd = open(buf, O_WRONLY);
	  if (fd < 0) {
#ifdef DEBUG
		  perror("gpio/direction");
#endif
		  return fd;
	  }
	  
	  r = write(fd, "in", 3);
	  close(fd);
	  if (r < 0) {
#ifdef DEBUG
		  perror("gpio/export");
#endif
		  return fd;
	  }
 
	  const char edge[] = "falling";
	  snprintf(buf, sizeof(buf), SYSFS_GPIO_DIR "/gpio%d/edge", gpio);
	  
	  fd = open(buf, O_WRONLY);
	  if (fd < 0) {
#ifdef DEBUG
		  perror("gpio/set-edge");
#endif
		  return fd;
	  }
	  
	  r = write(fd, edge, strlen(edge) + 1); 
	  close(fd);
	  if (r < 0) {
#ifdef DEBUG
		  perror("gpio/export");
#endif
		  return fd;
	  }
	  
	  snprintf(buf, sizeof(buf), SYSFS_GPIO_DIR "/gpio%d/value", gpio);
	  
	  fd = open(buf, O_RDONLY | O_NONBLOCK );
	  if (fd < 0) {
#ifdef DEBUG
		  perror("gpio/fd_open");
#endif
	  }
	  return fd;
}

void AD7705Comm::gpio_unexport(int gpio) {
	int fd, len;
	char buf[MAX_BUF];
	
	fd = open(SYSFS_GPIO_DIR "/unexport", O_WRONLY);
	if (fd < 0) {
#ifdef DEBUG
		perror("gpio/unexport");
#endif
	}
	
	len = snprintf(buf, sizeof(buf), "%d", gpio);
	int r = write(fd, buf, len);
	if (r < 0) {
#ifdef DEBUG
		perror("gpio/export");
#endif
	}

	close(fd);
}


int AD7705Comm::fdPoll(int gpio_fd, int timeout)
{
	struct pollfd fdset[1];
	int nfds = 1;
	int rc;
	char buf[MAX_BUF];
	
	memset((void*)fdset, 0, sizeof(fdset));
	
	fdset[0].fd = gpio_fd;
	fdset[0].events = POLLPRI;
	
	rc = poll(fdset, nfds, timeout);
	
	if (fdset[0].revents & POLLPRI) {
		// dummy read
		int r = read(fdset[0].fd, buf, MAX_BUF);
		if (r < 0) {
#ifdef DEBUG
			perror("gpio/export");
#endif
			return r;
		}
	}

	return rc;
}

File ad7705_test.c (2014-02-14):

/*
 * AD7705 test program for the Raspberry PI
 *
 * Copyright (c) 2007  MontaVista Software, Inc.
 * Copyright (c) 2007  Anton Vorontsov <avorontsov@ru.mvista.com>
 * Copyright (c) 2013  Bernd Porr <mail@berndporr.me.uk>
 *
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
 * Cross-compile with cross-gcc -I/path/to/cross-kernel/include
 */

#include <stdint.h>
#include <unistd.h>
#include <stdio.h>
#include <stdlib.h>
#include <fcntl.h>
#include <sys/ioctl.h>
#include <linux/types.h>
#include <linux/spi/spidev.h>

#include "gz_clk.h"

#define ARRAY_SIZE(a) (sizeof(a) / sizeof((a)[0]))

static void pabort(const char *s)
{
	perror(s);
	abort();
}

static const char *device = "/dev/spidev0.0";
static uint8_t mode = SPI_CPHA | SPI_CPOL;;
static uint8_t bits = 8;
static uint32_t speed = 50000;
static uint16_t delay = 10;
static int drdy_GPIO = 22; //RPI_V2_GPIO_P1_22;

static void writeReset(int fd)
{
	int ret;
	uint8_t tx1[5] = {0xff,0xff,0xff,0xff,0xff};
	uint8_t rx1[5] = {0};
	struct spi_ioc_transfer tr = {
		.tx_buf = (unsigned long)tx1,
		.rx_buf = (unsigned long)rx1,
		.len = ARRAY_SIZE(tx1),
		.delay_usecs = delay,
		.speed_hz = speed,
		.bits_per_word = bits,
	};

	ret = ioctl(fd, SPI_IOC_MESSAGE(1), &tr);
	if (ret < 1)
		pabort("can't send spi message");
}

static void writeReg(int fd, uint8_t v)
{
	int ret;
	uint8_t tx1[1];
	tx1[0] = v;
	uint8_t rx1[1] = {0};
	struct spi_ioc_transfer tr = {
		.tx_buf = (unsigned long)tx1,
		.rx_buf = (unsigned long)rx1,
		.len = ARRAY_SIZE(tx1),
		.delay_usecs = delay,
		.speed_hz = speed,
		.bits_per_word = bits,
	};

	ret = ioctl(fd, SPI_IOC_MESSAGE(1), &tr);
	if (ret < 1)
		pabort("can't send spi message");

}

static uint8_t readReg(int fd)
{
	int ret;
	uint8_t tx1[1];
	tx1[0] = 0;
	uint8_t rx1[1] = {0};
	struct spi_ioc_transfer tr = {
		.tx_buf = (unsigned long)tx1,
		.rx_buf = (unsigned long)rx1,
		.len = ARRAY_SIZE(tx1),
		.delay_usecs = delay,
		.speed_hz = speed,
		.bits_per_word = 8,
	};

	ret = ioctl(fd, SPI_IOC_MESSAGE(1), &tr);
	if (ret < 1)
	  pabort("can't send spi message");
	  
	return rx1[0];
}

static int readData(int fd)
{
	int ret;
	uint8_t tx1[2] = {0,0};
	uint8_t rx1[2] = {0,0};
	struct spi_ioc_transfer tr = {
		.tx_buf = (unsigned long)tx1,
		.rx_buf = (unsigned long)rx1,
		.len = ARRAY_SIZE(tx1),
		.delay_usecs = delay,
		.speed_hz = speed,
		.bits_per_word = 8,
	};

	ret = ioctl(fd, SPI_IOC_MESSAGE(1), &tr);
	if (ret < 1)
	  pabort("can't send spi message");
	  
	return (rx1[0]<<8)|(rx1[1]);
}


int main(int argc, char *argv[])
{
	int ret = 0;
	int fd;

	int no_tty = !isatty( fileno(stdout) );

	fd = open(device, O_RDWR);
	if (fd < 0)
		pabort("can't open device");

	/*
	 * spi mode
	 */
	ret = ioctl(fd, SPI_IOC_WR_MODE, &mode);
	if (ret == -1)
		pabort("can't set spi mode");

	ret = ioctl(fd, SPI_IOC_RD_MODE, &mode);
	if (ret == -1)
		pabort("can't get spi mode");

	/*
	 * bits per word
	 */
	ret = ioctl(fd, SPI_IOC_WR_BITS_PER_WORD, &bits);
	if (ret == -1)
		pabort("can't set bits per word");

	ret = ioctl(fd, SPI_IOC_RD_BITS_PER_WORD, &bits);
	if (ret == -1)
		pabort("can't get bits per word");

	/*
	 * max speed hz
	 */
	ret = ioctl(fd, SPI_IOC_WR_MAX_SPEED_HZ, &speed);
	if (ret == -1)
		pabort("can't set max speed hz");

	ret = ioctl(fd, SPI_IOC_RD_MAX_SPEED_HZ, &speed);
	if (ret == -1)
		pabort("can't get max speed hz");

	fprintf(stderr, "spi mode: %d\n", mode);
	fprintf(stderr, "bits per word: %d\n", bits);
	fprintf(stderr, "max speed: %d Hz (%d KHz)\n", speed, speed/1000);

	// enable master clock for the AD
	// divisor results in roughly 4.9MHz
	// this also inits the general purpose IO
	gz_clock_ena(GZ_CLK_5MHz,5);

	bcm2835_gpio_fsel(drdy_GPIO, BCM2835_GPIO_FSEL_INPT);

	// resets the AD7705 so that it expects a write to the communication register
	writeReset(fd);

	// tell the AD7705 that the next write will be to the clock register
	writeReg(fd,0x20);
	// write 00001100 : CLOCKDIV=1,CLK=1,expects 4.9152MHz input clock
	writeReg(fd,0x0C);

	// tell the AD7705 that the next write will be the setup register
	writeReg(fd,0x10);
	// intiates a self calibration and then after that starts converting
	writeReg(fd,0x40);

	// we read data in an endless loop and display it
	while (1) {
	  int d=0;
	  do {
	    // read /DRDY of the AD converter
	    d = bcm2835_gpio_lev(drdy_GPIO);
	    // loop while /DRDY is high
	  } while ( d );
	  
	  // tell the AD7705 to read the data register (16 bits)
	  writeReg(fd,0x38);
	  // read the data register by performing two 8 bit reads
	  int value = readData(fd)-0x8000;
		fprintf(stderr,"data = %d       \r",value);

		// if stdout is redirected to a file or pipe, output the data
		if( no_tty )
		{
			printf("%d\n", value);
			fflush(stdout);
		}
	}

	close(fd);

	return ret;
}

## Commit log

2014-02-14 Polling is now done via the GPIO pin 22 which connects to the DRDY pin of the AD converter. This should speed up reading from the AD drastically.
2018-02-02 Added the PCB design files
    [rpi_ad7705.brd, rpi_ad7705.sch, rpi_ad7705_bom.ods]
2020-01-29 Now properly with callbacks and the whole ADC routine in a class and thread.
2020-01-30 Updated circuit with an oscillator and new pin header.
    [rpi_ad7705.brd, rpi_ad7705.sch, rpi_ad7705_bom.ods]
2020-01-30 Switched the molex to the other side
    [rpi_ad7705.brd, rpi_ad7705.sch]
2020-03-20 Displays cached data in case UDP fails and is not crashing.
2021-03-25 Updated so that it tracks the current submodule
2023-03-02 Got rid of the static function for the thread

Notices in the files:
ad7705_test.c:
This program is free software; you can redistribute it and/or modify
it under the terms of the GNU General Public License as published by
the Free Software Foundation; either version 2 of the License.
